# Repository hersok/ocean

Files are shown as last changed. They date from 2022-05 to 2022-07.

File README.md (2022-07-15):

# O.C.E.A.N. – Open-Hardware Concentration Estimation and Numeration

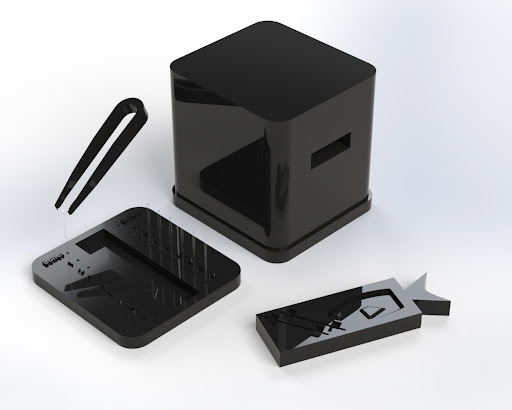
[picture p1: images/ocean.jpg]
Open-Hardware Concentration Estimation and Numeration
> 

### What is O.C.E.A.N.?

O.C.E.A.N. stands for Open-Hardware Concentration Estimation and Numeration.

O.C.E.A.N. is a low-cost, open-hardware device for measuring the concentration of liquid samples for cryogenic processing

### Why is concentration measurement important?

Concentration measurements ensure quality management at several crucial steps in the cryopreservation process.

### What is Open-Hardware?

Open-Hardware is an emerging movement in scientific research that aims to create freely available, iterative, and community-based designs for manufacturing labware, thereby lowering cost barriers to research.

### Why is the cryopreservation of fish and aquatic species' germplasm important?

1. Food security

2. Biomedical research

3. Genetic Biodiversity

### What is a short summary of this project?

Open-Hardware Concentration Estimation and Numeration, O.C.E.A.N., is an open-hardware device for measuring the cell concentration of fish germplasm samples to provide quality management in cryogenic research processes. The cryopreservation of fish and aquatic species’ germplasm is central to food security, biomedical research, and for maintaining genetic biodiversity. At present, the aquatic species cryopreservation process is impeded by the absence of low-cost, accessible devices for concentration measurement of low-volume samples. O.C.E.A.N. is an open-hardware device that seeks to address the current barriers to concentration measurement, as current methods may be expensive, time-intensive, and exclusive to select processing centers. Our device can be successfully used to generate a calibration curve for known concentrations. After generating this curve, the device makes it possible to measure the concentration of 5 µL fish sperm samples. The 3D Design files are openly available for download on GitHub, allowing for anyone with access to a 3D-printer, photocell, LED, and Arduino UNO board, to replicate and iterate on our results.

### Open-source License

This open hardware project is licensed by the Creative Commons `Attribution-NonCommercial-ShareAlike 4.0 International (CC BY-NC-SA 4.0)` License

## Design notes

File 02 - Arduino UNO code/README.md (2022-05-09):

# Arduino Code

## Background

For this project, our group used the following microcontrollers:

1. Arduino UNO

2. Arduino UNO WiFi Rev 2

---

## Uploading code files to Arduino Device

Please see the instructions below for how we uploaded `.ino` code files to the respective Arduino UNO boards:

### Connect the Arduino UNO device to your computer

1. Obtain a **USB-B to USB-A cable**

2. Connect one end to the Arduino UNO's USB-B port

3. Connect the other end to your computer's USB-port

### Uploading files to the Arduino UNO board

#### Arduino UNO

1. Download and install the Arduino IDE from https://www.arduino.cc/en/software

2. Open the Arduino IDE

3. Go to "File > Open" to open a particular file

4. Compile the code using the "Verify" checkmark button near the top of the IDE.

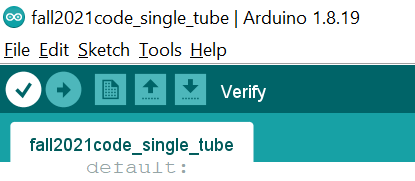
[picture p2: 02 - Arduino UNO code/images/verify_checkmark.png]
Compile the code using the Verify button
> 

5. Ensure that the Arduino UNO board is plugged into your computer via USB. Please see instructions [here](#Connect-the-Arduino-UNO-device-to-your-computer)

6. Ensure that the correct type of board is configured in the Arduino IDE

7. Go to "Tools > Board > Arduino AVR Boards > Arduino UNO "

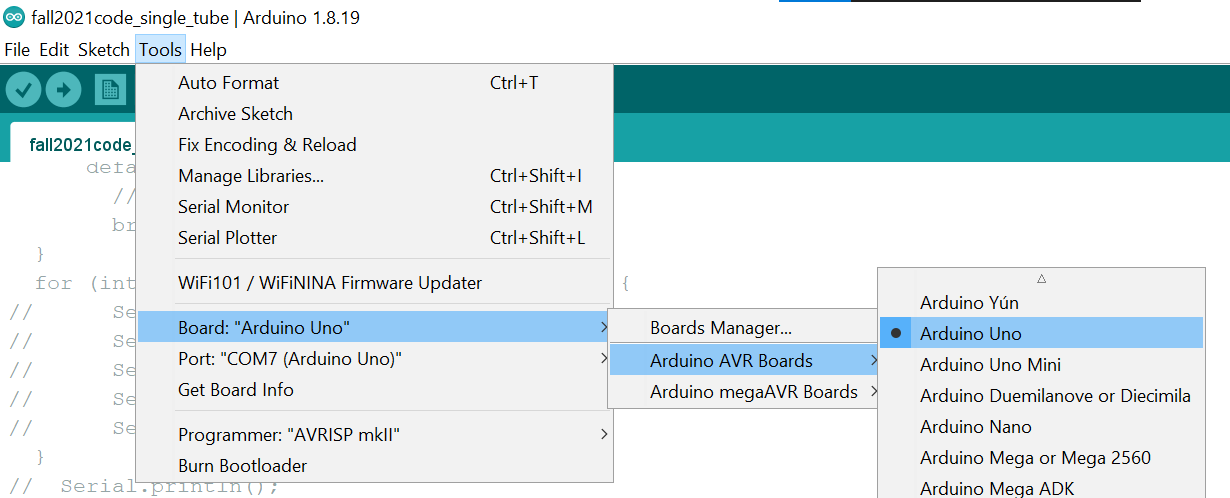
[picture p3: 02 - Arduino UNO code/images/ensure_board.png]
Select the appropriate board
> 

8. Ensure that the correct COM port is selected

9. Go to "Tools > Port" and select the Serial port alongside "Arduino UNO" in parentheses. For example, in the picture below, it is "COM7 (Arduino UNO)"

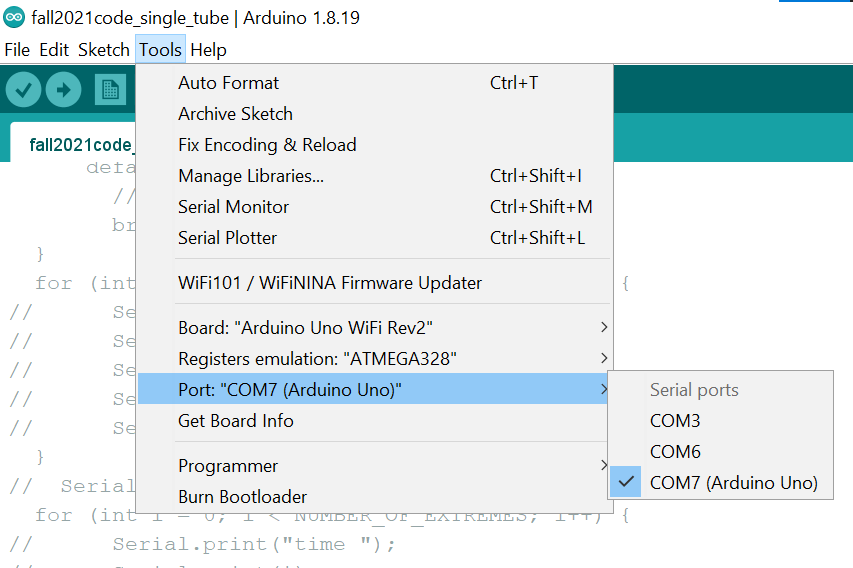
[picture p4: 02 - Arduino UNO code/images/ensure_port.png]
Select the appropriate port
> 

10. Upload the code to the Arduino UNO using the right-arrow upload button at the top of the page.

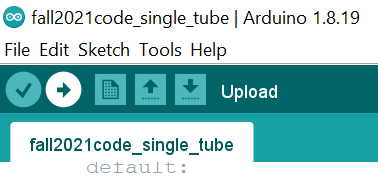
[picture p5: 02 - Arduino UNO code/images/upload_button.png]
> 

<!-- #### Arduino UNO WiFi -->

<!-- # Using KiTTY software to save Arduino Serial Monitor output -->

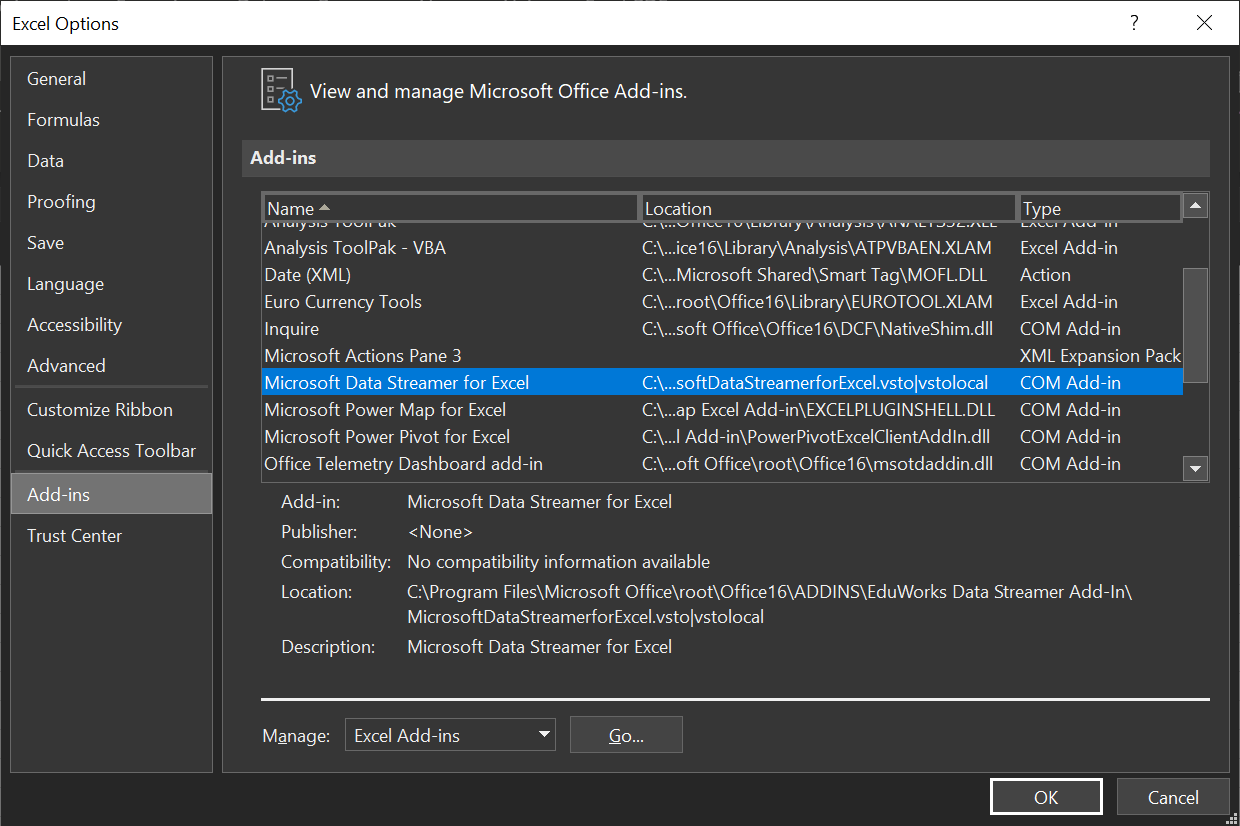
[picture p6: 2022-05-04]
02 - Arduino UNO code/images/excel data streamer option menu.png

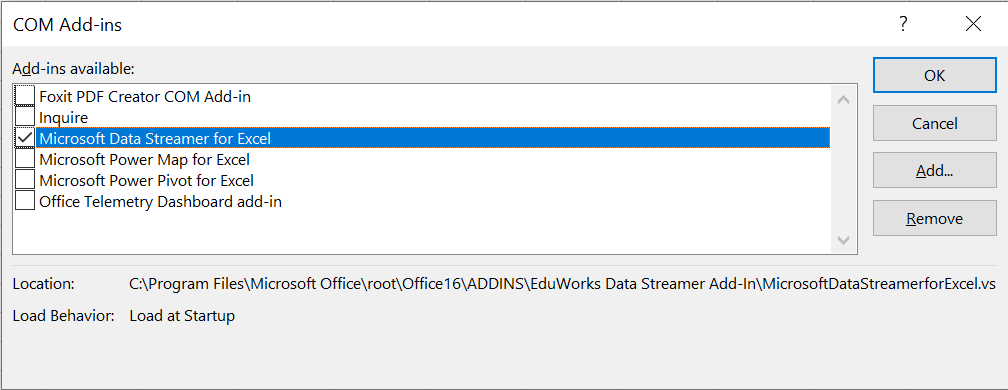
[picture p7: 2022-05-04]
02 - Arduino UNO code/images/dialog_box.png

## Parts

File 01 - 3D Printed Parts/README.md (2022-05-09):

# 3D Printed Parts

## Description

This folder contains all of the 3D-printed parts for O.C.E.A.N.

All parts were designed in SolidWorks

## Contents

This directory contains three folders, each with 13 parts:

1. `*.SLDPRT`

    * These are the original SolidWorks files. Please use these files if you would like to change an aspect of the design!

2. `*.STL`

    * The unit for these STL files is inches. Please use these files if you would like to print the device!

3. `*.3MF`

    * This is an alternative type of file for 3D printing that contains unit information.

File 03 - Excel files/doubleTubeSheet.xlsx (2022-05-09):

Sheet: userInterface
What are you measuring? |  | Do you already know the concentration? |  |  | What is your name?
Fish Sperm | solutions | Yes | is my answer |  | John Doe | is my name
What type of fish? |  | If yes, what's the type of concentration? |  |  | What is your affiliation?
Goldfish | is my fish type | Nominal | concentration |  | LSU AgCenter | is my lab's name
What is the purpose of your measurement? |  | What are the units of your concentration? |  |  | What is your Sample's ID number?
Calibration | is my intent | g/mL | are the units | C- | 100 | is the Sample ID
What is the volume of your sample? |  | What is your sample's concentration? |  |  | Data Streamer:
5 | uL | 0.2 | g/mL |  | Buffer: | 371
 |  |  |  |  | Sample: | 376

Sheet: calibrationData
Index | Date | Time | Buffer Peak | Sample Peak | Sample Type | Fish Type | Concentration Known | Concentration Type | Concentration | Units | Meas. Purpose | Sample Volume (uL) | User Name | Lab Name | Sample ID
1 | 2022-May-06 | 1899-12-30 | 371 | 376 | Fish Sperm | Goldfish | Yes | Nominal | 0.2 | g/mL | Calibration | 5 | John Doe | LSU AgCenter | C-100

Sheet: measurementData
Index | Date | Time | Buffer Peak | Sample Peak | Sample Type | Fish Type | Concentration Known | Concentration Type | Concentration | Units | Meas. Purpose | Sample Volume (uL) | User Name | Lab Name | Sample ID
1 | 2022-May-06 | 1899-12-30 | 371 | 376 | Fish Sperm | Goldfish | Yes | Nominal | 0.2 | g/mL | Measurement | 5 | John Doe | LSU AgCenter | M-100

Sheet: Data In
Data In (From Arduino Uno (COM7))
Data coming from the current data source will appear below as it is received.
Current Data
TIME | CH1 | CH2 | CH3 | CH4 | CH5 | CH6 | CH7 | CH8 | CH9 | CH10
44687.34931 | 371 | 376
Historical Data
TIME | CH1 | CH2 | CH3 | CH4 | CH5 | CH6 | CH7 | CH8 | CH9 | CH10
44687.34918 | 375 | 384
44687.34931 | 371 | 376

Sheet: Data Out
Data Out (To Device)
Data entered into the channels below will be sent to the currently connected device as a comma-delimited string.
CH1 | CH2 | CH3 | CH4 | CH5 | CH6 | CH7 | CH8 | CH9 | CH10

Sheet: Settings
Workbook Settings
Settings below will affect how data is read into the current workbook from data sources. Clear a field's contents to revert to its default setting.
Data interval (ms) | 150 | 150
Data rows | 15 | 15
Data channels | 10 | 10
Data orientation | Newest last | Newest last
WARNING: Changing settings may result in the loss of content and/or custom formatting in the Data In and Data Out worksheets. Always save before changing values.

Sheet: Manifest
Arduino Uno |  |  |  |  |  |  |  |  | {"Channels":[{"Description":null,"Id":null,"IsGhost":false,"Name":null,"Status":"Active","SubChannels":[{"Description":null,"Id":"CH1","IsGhost":false,"Name":"CH1","Status":"Active","SubChannels":[],"UnitOfMeasure":null},{"Description":null,"Id":"CH2","IsGhost":false,"Name":"CH2","Status":"Active","SubChannels":[],"UnitOfMeasure":null},{"Description":null,"Id":"CH3","IsGhost":false,"Name":"CH3","Status":"Active","SubChannels":[],"UnitOfMeasure":null},{"Description":null,"Id":"CH4","IsGhost":false,"Name":"CH4","Status":"Active","SubChannels":[],"UnitOfMeasure":null},{"Description":null,"Id":"CH5","IsGhost":false,"Name":"CH5","Status":"Active","SubChannels":[],"UnitOfMeasure":null},{"Description":null,"Id":"CH6","IsGhost":false,"Name":"CH6","Status":"Active","SubChannels":[],"UnitOfMeasure":null},{"Description":null,"Id":"CH7","IsGhost":false,"Name":"CH7","Status":"Active","SubChannels":[],"UnitOfMeasure":null},{"Description":null,"Id":"CH8","IsGhost":false,"Name":"CH8","Status":"Active","SubChannels":[],"UnitOfMeasure":null},{"Description":null,"Id":"CH9","IsGhost":false,"Name":"CH9","Status":"Active","SubChannels":[],"UnitOfMeasure":null},{"Description":null,"Id":"CH10","IsGhost":false,"Name":"CH10","Status":"Active","SubChannels":[],"UnitOfMeasure":null}],"UnitOfMeasure":null}],"Commands":[],"DataInterval":150,"Id":"3EB6B8E7-BFE3-4EF6-AA1D-74373D2929EC","IsGenerated":true,"Name":"Arduino Uno","Version":null,"BaudRate":115200}
This manifest was generated for the connected device. You can edit the device name and channel data here and the Data In worksheet will be updated.
 | Channels
 |  |  |  |  |  |  | Data Source Id
 |  | Id | Name | Description | Unit of Measure | Active | 3EB6B8E7-BFE3-4EF6-AA1D-74373D2929EC | 1
 |  | CH1 | CH1 |  |  | ü | Data Interval (ms)
 |  | CH2 | CH2 |  |  | ü | 150
 |  | CH3 | CH3 |  |  | ü | Baud Rate
 |  | CH4 | CH4 |  |  | ü | 115200
 |  | CH5 | CH5 |  |  | ü
 |  | CH6 | CH6 |  |  | ü
 |  | CH7 | CH7 |  |  | ü
 |  | CH8 | CH8 |  |  | ü
 |  | CH9 | CH9 |  |  | ü
 |  | CH10 | CH10 |  |  | ü

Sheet: menuOptions
Total Time Options | Sampling Options | Affliation Options | Measurement Type Options | Fish Options | Binary Options | Concentration Type Options | Concentration Units Options | Purpose Options | Volume Options | Concentration Options
1 | 1 | Louisiana State University | Powdered Milk | Zebrafish | Yes | Nominal | g/mL | Calibration | 1 | N/A
2 | 2 | LSU AgCenter | Fish Sperm | Catfish | No | Exact | cells/mL | Measurement | 2 | 3
5 | 5 |  |  | Salmon |  |  |  |  | 3 | 2
10 | 10 |  |  | Carp |  |  |  |  | 4 | 1
15 | 20 |  |  | N/A |  |  |  |  | 5 | 0.75
20 | 30 |  |  | Goldfish |  |  |  |  | 6 | 0.5
25 | 40 |  |  |  |  |  |  |  | 7 | 0.25
30 | 50 |  |  |  |  |  |  |  | 8 | 0.2
60 | 100 |  |  |  |  |  |  |  | 9 | 0.125
 |  |  |  |  |  |  |  |  | 10 | 0.1
 |  |  |  |  |  |  |  |  | 15 | 0.05
 |  |  |  |  |  |  |  |  | 20 | 0.025
 |  |  |  |  |  |  |  |  | 25 | 0.02
 |  |  |  |  |  |  |  |  | 30 | 0.01
 |  |  |  |  |  |  |  |  | 50

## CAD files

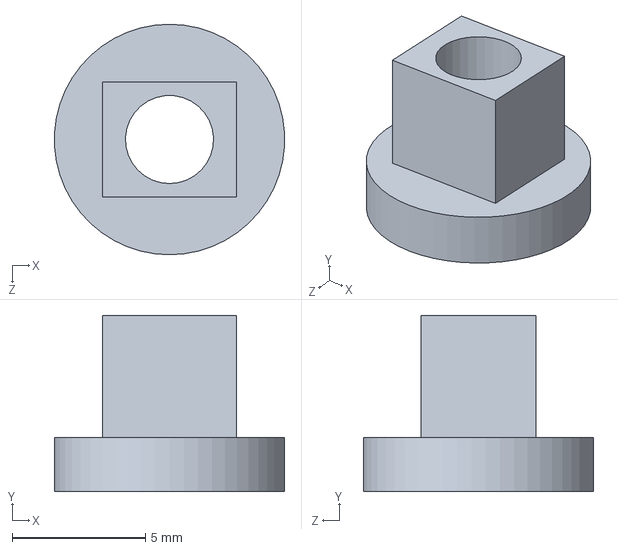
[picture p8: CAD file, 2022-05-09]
01 - 3D Printed Parts/SLDPRT/Sensor Cap.SLDPRT
8.62 x 6.60 x 8.64 mm

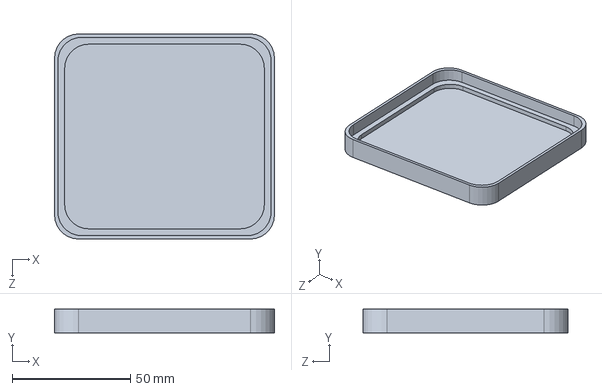
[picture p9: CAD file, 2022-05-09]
01 - 3D Printed Parts/SLDPRT/Base.SLDPRT
93.2 x 10.2 x 86.9 mm

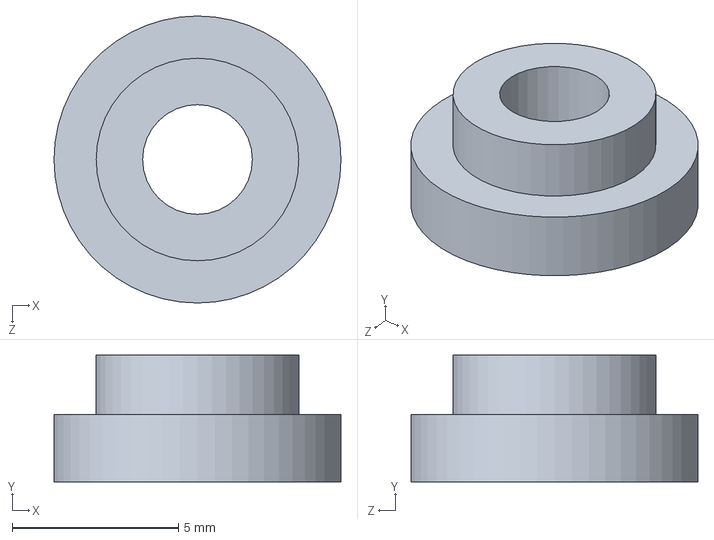
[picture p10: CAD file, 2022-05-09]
01 - 3D Printed Parts/SLDPRT/LED Cap.SLDPRT
8.64 x 3.81 x 8.64 mm

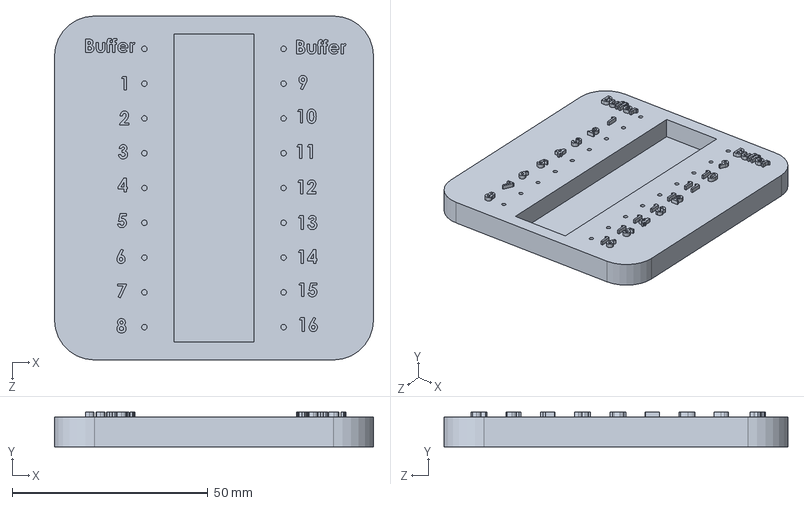
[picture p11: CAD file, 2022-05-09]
01 - 3D Printed Parts/SLDPRT/Tube Holding Tray.SLDPRT
81.5 x 8.89 x 87.9 mm

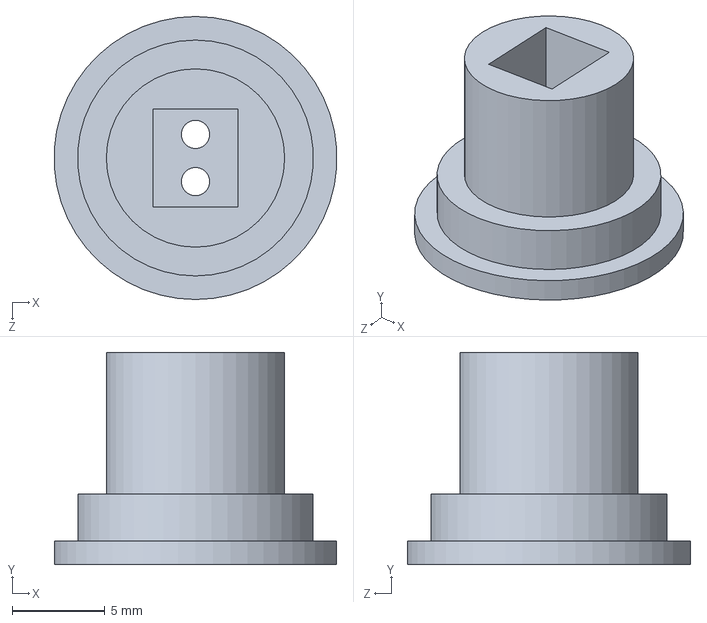
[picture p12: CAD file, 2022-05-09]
01 - 3D Printed Parts/SLDPRT/Sensor Holder.SLDPRT
15.2 x 11.4 x 15.2 mm

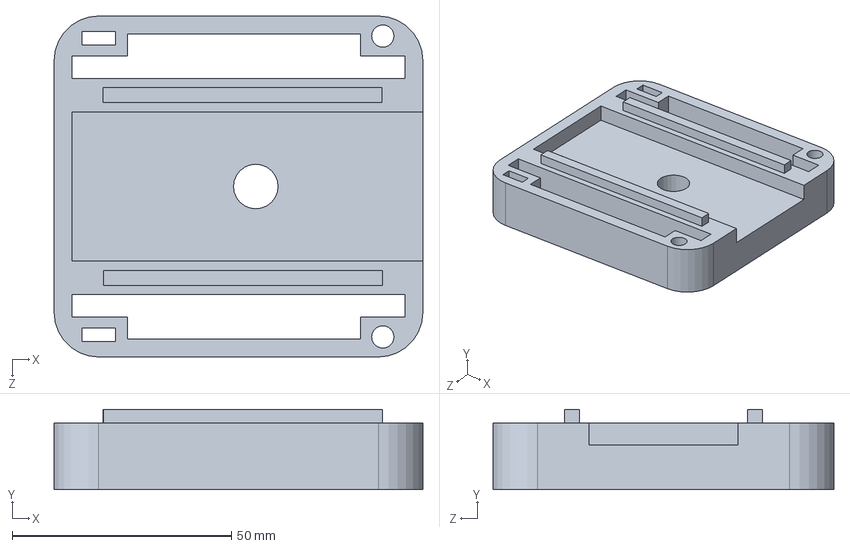
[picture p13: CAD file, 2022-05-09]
01 - 3D Printed Parts/SLDPRT/LED Shelf.SLDPRT
84.1 x 18.3 x 77.7 mm

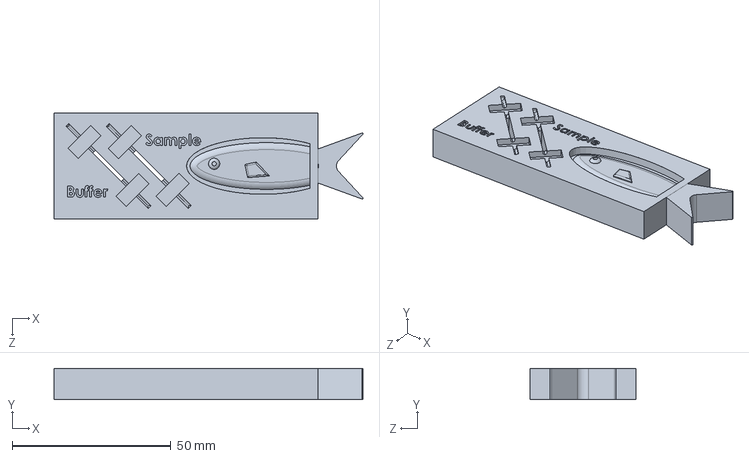
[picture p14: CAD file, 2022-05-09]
01 - 3D Printed Parts/SLDPRT/Tube Drawer.SLDPRT
97.3 x 9.91 x 33.4 mm

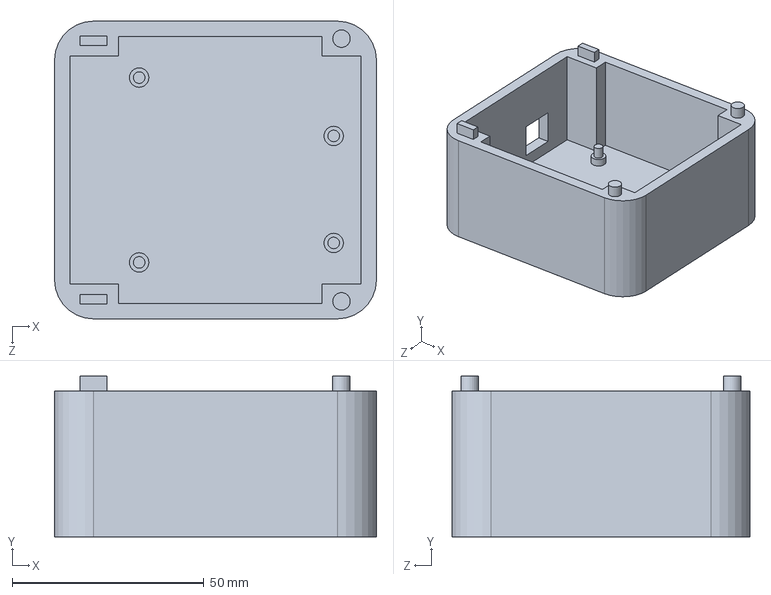
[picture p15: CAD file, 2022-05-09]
01 - 3D Printed Parts/SLDPRT/Arduino Shelf.SLDPRT
84.1 x 41.9 x 77.7 mm

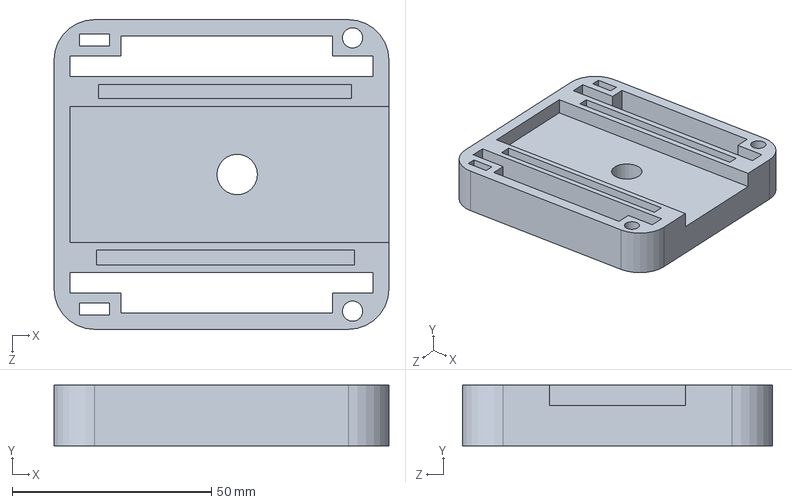
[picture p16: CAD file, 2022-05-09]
01 - 3D Printed Parts/SLDPRT/Sensor Shelf.SLDPRT
84.1 x 15.2 x 77.7 mm

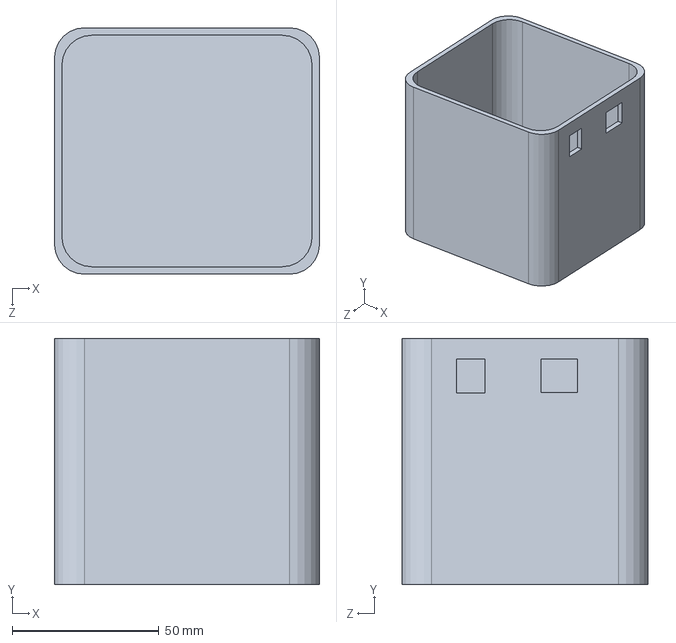
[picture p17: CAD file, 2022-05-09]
01 - 3D Printed Parts/SLDPRT/Cover.SLDPRT
90.4 x 84.1 x 84.1 mm

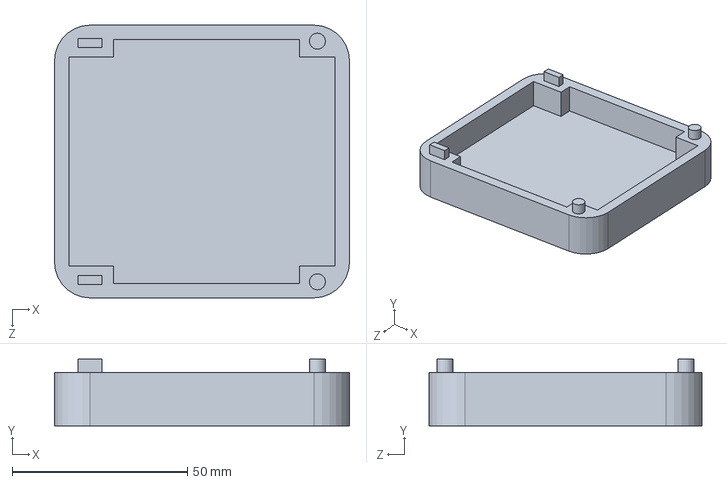
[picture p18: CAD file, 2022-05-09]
01 - 3D Printed Parts/SLDPRT/Top Shelf.SLDPRT
84.1 x 19.1 x 77.7 mm

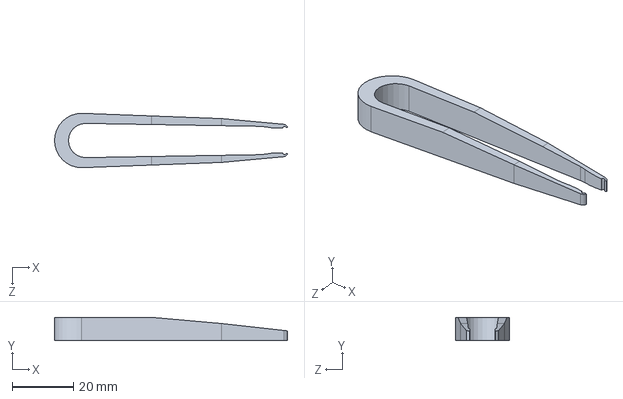
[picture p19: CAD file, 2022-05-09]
01 - 3D Printed Parts/SLDPRT/Tube Tweezer.SLDPRT
76.2 x 7.62 x 17.8 mm

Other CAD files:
01 - 3D Printed Parts/SLDPRT/LED Holder.SLDPRT
01 - 3D Printed Parts/3MF/Arduino Shelf.3MF
01 - 3D Printed Parts/3MF/Base.3MF
01 - 3D Printed Parts/3MF/Cover.3MF
01 - 3D Printed Parts/3MF/LED Cap.3MF
01 - 3D Printed Parts/3MF/LED Holder.3MF
01 - 3D Printed Parts/3MF/LED Shelf.3MF
01 - 3D Printed Parts/3MF/Sensor Cap.3MF
01 - 3D Printed Parts/3MF/Sensor Holder.3MF
01 - 3D Printed Parts/3MF/Sensor Shelf.3MF
01 - 3D Printed Parts/3MF/Top Shelf.3MF
01 - 3D Printed Parts/3MF/Tube Drawer.3MF
01 - 3D Printed Parts/3MF/Tube Holding Tray.3MF
01 - 3D Printed Parts/3MF/Tube Tweezer.3MF
01 - 3D Printed Parts/STL/Arduino Shelf.STL
01 - 3D Printed Parts/STL/Base.STL
01 - 3D Printed Parts/STL/Cover.STL
01 - 3D Printed Parts/STL/LED Cap.STL
01 - 3D Printed Parts/STL/LED Holder.STL
01 - 3D Printed Parts/STL/LED Shelf.STL
01 - 3D Printed Parts/STL/Sensor Cap.STL
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

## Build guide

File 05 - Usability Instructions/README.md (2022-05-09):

# Usability Instructions

## Preparing the device for measurements

1. Assemble the O.C.E.A.N. device as in the `04 - Assembly Instructions` folder.

2. Obtain glass microcapillary tubes to hold liquid samples. Our team used the following tubes:

    * Name: Drummond Scientific MicroCaps
    * Description: 100 Disposable 5μL micropipettes
    * CAT. No. 1-000-0050
    * Capacity: 5 μL
    * Length (mm): 32
    * Relative O.D.: 0.037 in
    * Relative I.D.: 0.0176 in
    * Manufacturer website: https://www.drummondsci.com/product/capillary-micropipettes/microcaps/

3. Upload the corresponding Arduino code file from the `02 - Arduino UNO code` folder. Instructions for how to upload are explained in the `README` file located in the same folder.

## Taking Measurements

1. Choose a method [here](#Saving-Results) for saving measurement results

2. Load a capillary tube containing your buffer solution into the designated slot on the testing drawer.

3. Load a capillary tube containing your sample into the designated slot.

4. Partially insert the testing drawer into the drawer slot until it does not fall out.

5. Open either the Arduino Serial Monitor or the provided MS Excel file

6. Ensure the Arduino UNO is plugged into the computer

7. Slowly insert the testing drawer into the device for a duration of 10 to 15 seconds. Slowly retract the testing drawer for a duration of 10 to 15 seconds.

8. Record the saved results, which should be in the output format of `Buffer Peak, Sample Peak`

## Saving Results

### MS Excel Data Streamer

1. Please follow the instructions linked below for how to "Enable the Data Streamer add-in" for MS Excel

> https://support.microsoft.com/en-us/office/enable-the-data-streamer-add-in-70052b28-3b00-41e7-8ab6-8a9f142dffeb

2. Download the `doubleTubeSheet.xlsx` file from the `03 - Excel files` folder

3. Open the `doubleTubeSheet.xlsx` file.

4. Navigate to the `Data Streamer` tab at the top of the Excel interface

5. Ensure the Arduino Uno is plugged into the computer

6. Select `Connect a Device` and click on the correct Arduino UNO device

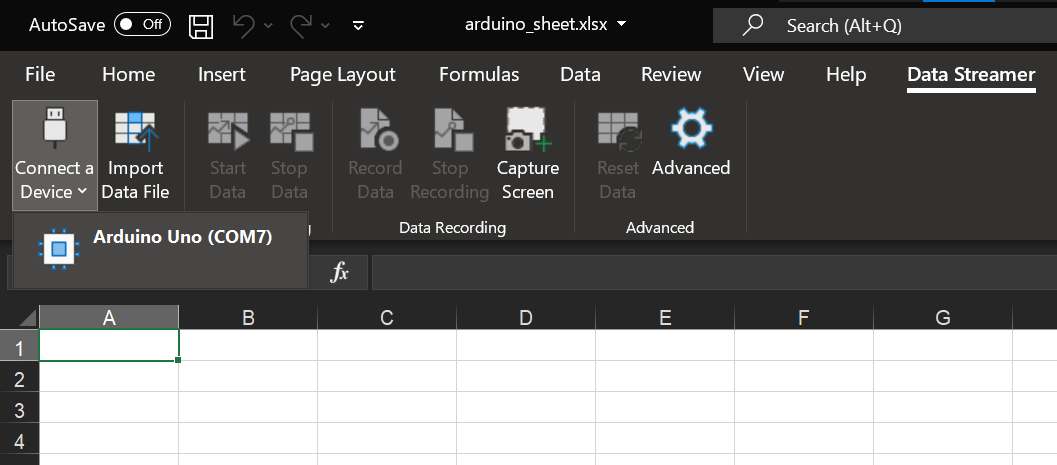
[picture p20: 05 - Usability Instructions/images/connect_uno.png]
Connect the Arduino UNO to MS Excel
> 

7. Press the `Advanced` settings cog > Navigate to `Settings tab` > Select the appropriate COM port > Change the Baud Rate to `115200`

8. Click on the `Start Data` button to begin collecting data

9. Navigate to the `userInterface` worksheet on Excel and change the values to your liking

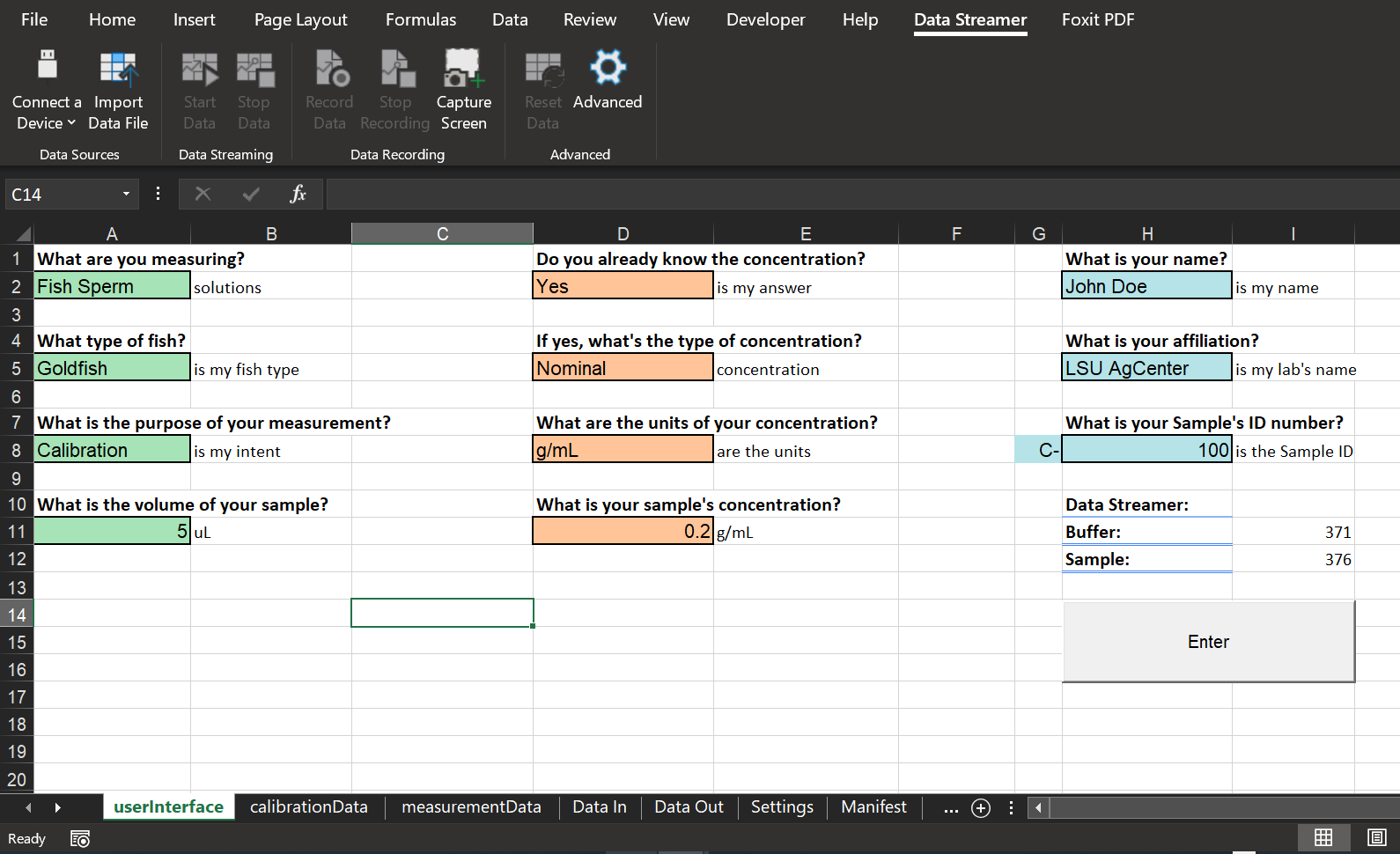
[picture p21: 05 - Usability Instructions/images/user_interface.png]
> 

10. Take a measurement per the instructions [here](#Taking-Measurements)

11. Press the Enter button

12. Navigate to either the `calibrationData` or `measurementData` worksheet to see your results

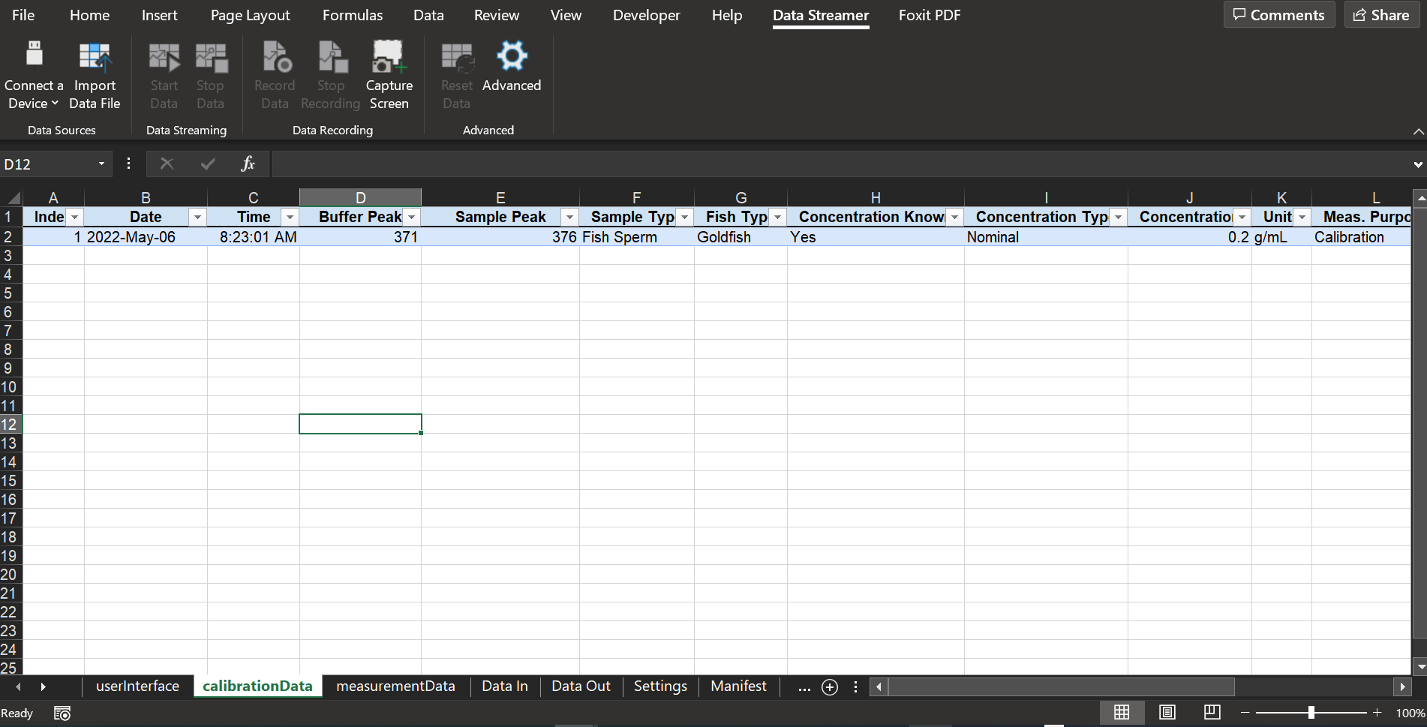
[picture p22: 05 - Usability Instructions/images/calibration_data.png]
> 

### Arduino IDE Serial Monitor

1. Open the Arduino IDE

2. Upload the corresponding Arduino code file from the `02 - Arduino UNO code` folder

3. Navigate to `Tools` > `Serial Monitor` to open the Serial Monitor

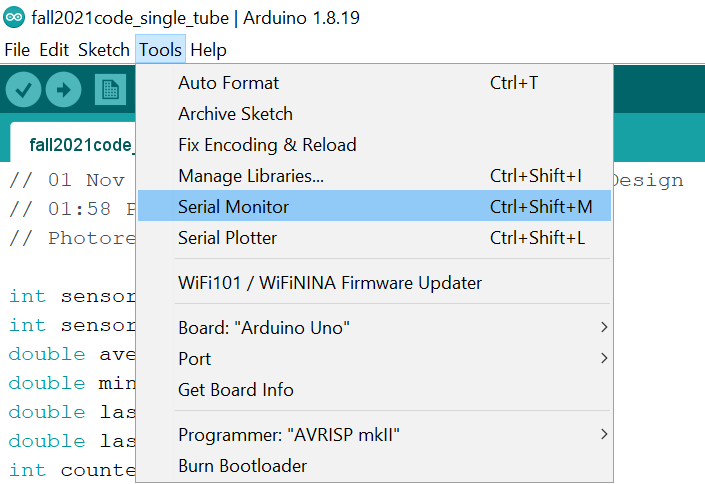
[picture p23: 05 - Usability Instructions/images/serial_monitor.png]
The Serial Monitor menu
> 

4. Ensure that the baud rates match by selecting the correct baud rate (115200 baud) from the dropdown menu in the lower right corner of the window.

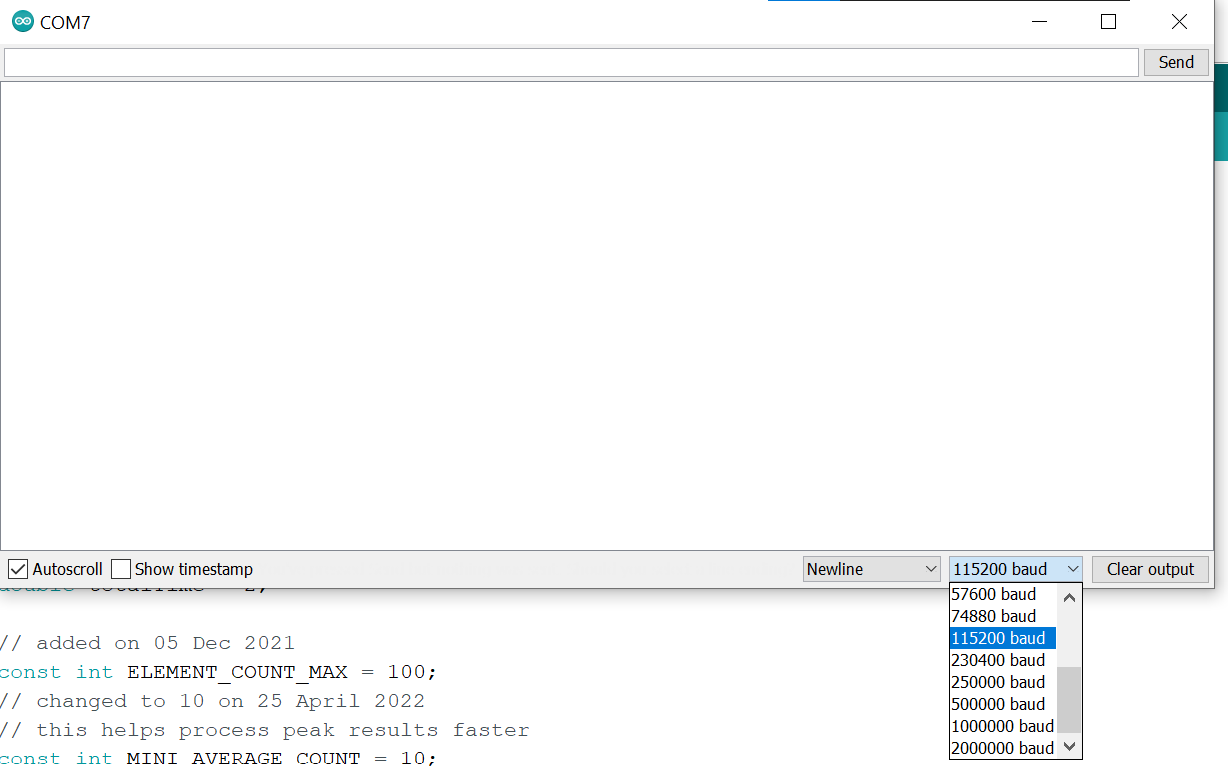
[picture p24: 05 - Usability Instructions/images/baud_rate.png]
Change the baud rate to 115200
> 

## 1. Creating a Calibration Curve

1. Follow the instructions in the [Taking Measurements](#Taking-Measurements) section to measure and record values for 10 to 16 different concentrations of the test sample.

2. Download and open the `calibrationDashboard` file from the `03 - Excel files` folder

3. Input the measured peak values for the buffer and sample solutions

4. Input the Offset and Sensitivity values from the best-fit curve into cells `J25` and `J28`

## 2. Measuring the Concentration of New Samples

1. With the `calibrationDashboard` file open in Excel, navigate to the `Detecting Concentrations for Solute #1`

2. Take a measurement (instructions [here](#Taking-Measurements)) of the solution you would like to know the concentration of

3. Input the measured `Max Buffer Peak` and `Max Sample Peak` into the corresponding cells on the spreadsheet to calculate the concentration

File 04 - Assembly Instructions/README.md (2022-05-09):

# Assembly Instructions

## Physical Device Assembly

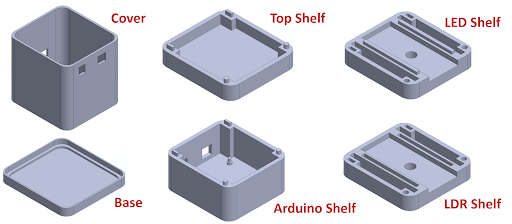
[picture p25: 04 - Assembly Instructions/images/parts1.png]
Parts Picture 1
> 

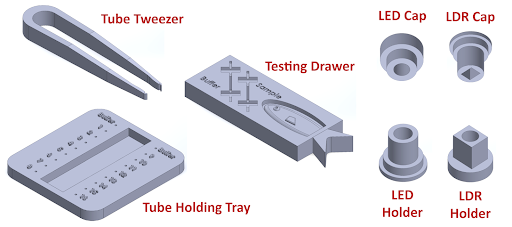
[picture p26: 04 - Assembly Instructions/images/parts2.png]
Parts Picture 2
> 

1. Install the Arduino UNO board onto the Arduino shelf, using the provided mounting features.

2. Assemble the breadboard circuit as shown. Our team used 20cm long female-to-male jumper wires in order to connect the LED and light-dependent resistor (LDR).

3. Install jumper wires leading from the breadboard to the Arduino UNO's `5V power`, `ground`, and `A0` ports.

4. First, install the LDR into the LDR Cap, then, assemble with the LDR Holder. Insert this subassembly into the LDR shelf.

5. Assemble the LDR shelf to the top of the Arduino shelf. These parts have asymmetrical mating features so that the parts can only be assembled one way...the right way!

6. First, install the LED into the LED Cap, then, assemble with the LED Holder. Insert this subassembly into the LED shelf.

7. Assemble the LED shelf to the top of the LDR shelf.

8. Assemble the top shelf to the existing assembly.

9. Move the existing assembly to rest on the base piece.

10. Assemble the cover so that it covers the existing assembly and snaps into the base.

11. Get ready to measure concentrations!

## Circuit Assembly

### Circuit Diagram

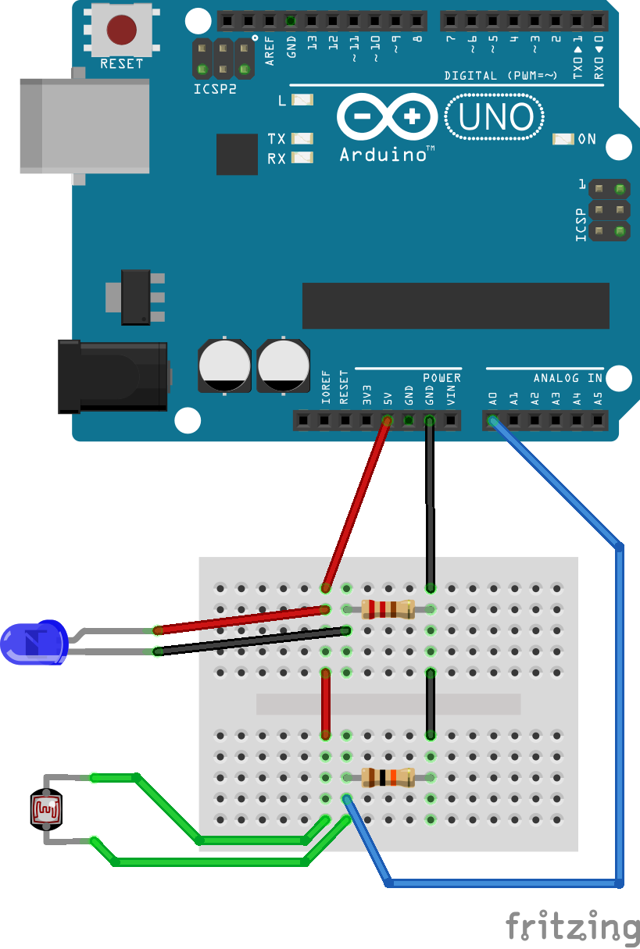
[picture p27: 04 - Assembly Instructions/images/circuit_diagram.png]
Arduino Circuit assembly
> 

### Circuit Schematic

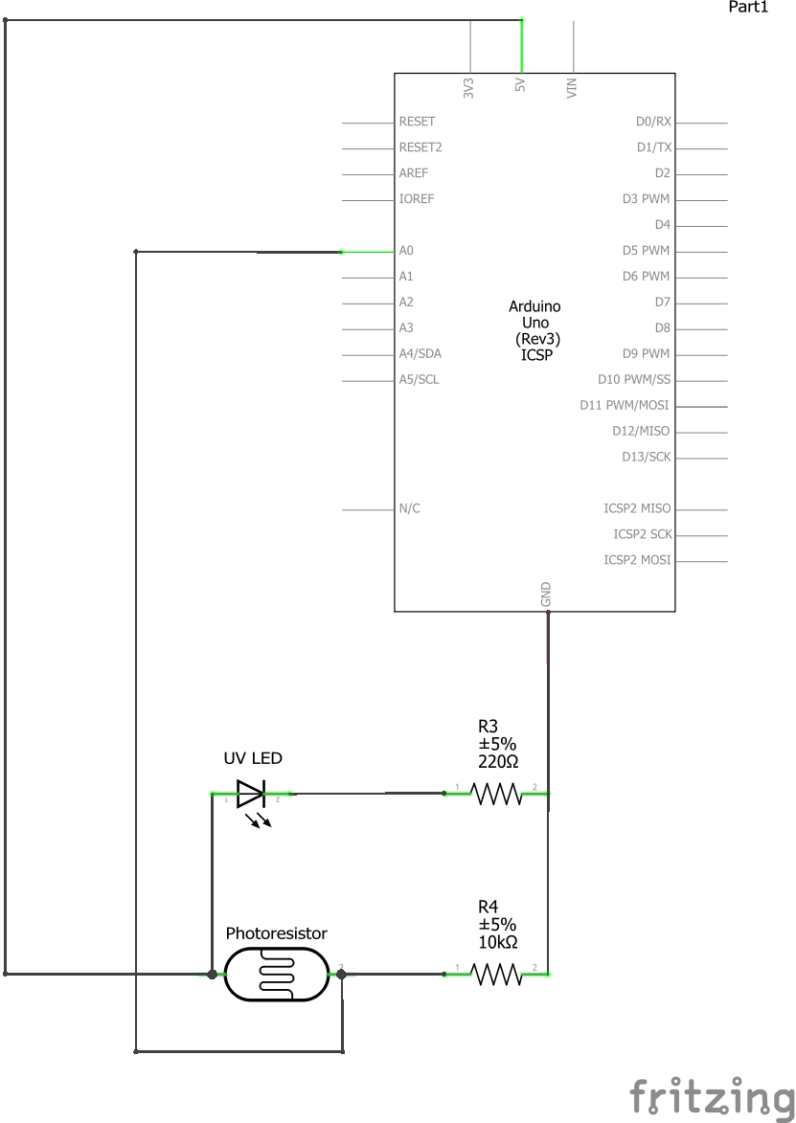
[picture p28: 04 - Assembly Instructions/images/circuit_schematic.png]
Arduino Circuit schematic
> 

### Parts required

1. UV LED (watch out for the direction of the positive lead!)

2. Light-dependent resistor

3. 100-300 Ohm resistor (220 Ohm in our case)

4. 5000-10000 Ohm resistor (10k Ohm in our case)

5. Wires (we used a combination of male-to-male and female-to-male 20cm long jumper wires)

6. Arduino UNO board

7. USB-B to USB-A cable

8. Breadboard (the above diagram is for a mini breadboard, which fits inside the device. However, the circuit may be assembled without the help of a breadboard, so long that the photocell and LED are connected in parallel, as shown in the schematic above.)

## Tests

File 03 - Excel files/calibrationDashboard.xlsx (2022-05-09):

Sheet: Calibration for Solute #1
 | Table 1 | Sperm Cells / mL
Step 1: Calibrate Device for Solute | Concentration # | Known Concentration | Max Buffer Peak | Max Sample Peak | Date | Time
Use solute that you seek to determine concentration of in future use of device (ex. powdered milk, specific species) | 1 | 4800000000 | 393 | 105 | 2022-05-04 | 13:03:01
 | 2 | 2400000000 | 375 | 135 | 2022-05-04 | 13:28:43
1. Use up to 16 known sample concentrations to calibrate device. More known concentrations = better calibration | 3 | 1200000000 | 395 | 204 | 2022-05-04 | 13:30:10
 | 4 | 600000000 | 389 | 278 | 2022-05-04 | 13:32:17
2. Collect each sample concentration with seperate capillary tubes and put in numbered slots on holding tray | 5 | 300000000 | 388 | 329 | 2022-05-04 | 13:34:39
 | 6 | 150000000 | 397 | 350 | 2022-05-04 | 13:35:14 | All 14
3. Collect buffer or solvent in a capillary tube and put in "buffer" slot on test drawer | 7 | 75000000 | 390 | 370 | 2022-05-04 | 13:42:05
 | 8 | 37500000 | 393 | 368 | 2022-05-04 | 13:44:49
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

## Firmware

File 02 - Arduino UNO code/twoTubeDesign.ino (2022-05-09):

//
// Copyright 2022
//
// publish date: 03 May 2022, Tuesday, at 11:41 AM
// version 1 of code
// to do: add timestamp to output
//
// this code:
// outputs peak values for the two-tube design
//

int sensorPin = A0;
int sensorValue = 0;
double valuesAverage = 0;
int counter = 0;
double delayVal = 1000;
// total time for testing (in seconds)
double totalTime = 0.1;

const int ELEMENT_COUNT_MAX = 100;
// the sampling time is totalTime / ELEMENT_COUNT_MAX
// for example, this code takes measurements every 0.1/100 = 0.001 seconds
double values[ELEMENT_COUNT_MAX];

const int NUMBER_OF_EXTREMES = 4;
double extremes[NUMBER_OF_EXTREMES];
double times[NUMBER_OF_EXTREMES];

// when the sensorValue crosses the monitoringThreshold,
// the code starts to look for peak values to record
const double monitoringThreshold = 0.03;
double thresholdValue = 0;
int maxValue = 0;
int numberOfPeak = 0;
double lastAverage = 0;
bool resetTracker = true;
int currentIndex = 0;

void setup() {
  Serial.begin(115200);
  for (int i = 0; i < ELEMENT_COUNT_MAX; i++) {
   values[i] = 0;
  }
  delayVal = delayVal / (ELEMENT_COUNT_MAX/totalTime);
}

void loop() {
  sensorValue = analogRead(sensorPin);
  delay(delayVal);
  counter = counter + 1;
  // debugging purposes: prints out the sensor value
  // Serial.println(sensorValue);

  valuesAverage = valuesAverage + sensorValue;
  values[counter - 1] = sensorValue;

  // once the values array is full,
  // this calculates the average of its values
  if (counter == ELEMENT_COUNT_MAX) {
    valuesAverage = valuesAverage / counter;
    lastAverage = valuesAverage;
    valuesAverage = 0;
    counter = 0;
  }

// switch statement that coordinates the logic for saving peak values
  switch (numberOfPeak) {
      case 0:
          if (sensorValue > maxValue) {
              maxValue = sensorValue;
          }
          thresholdValue = (maxValue - 0) * monitoringThreshold;
          if (sensorValue < thresholdValue) {
              if ((lastAverage - sensorValue) > 0) {
                  numberOfPeak = 1;
              }
          }
          break;
      case 1:
          // Serial.println("You crossed the threshold, going from high to low");
          if (resetTracker) {
              maxValue = 0;
              resetTracker = false;
          }
          if (sensorValue > thresholdValue) {
              if ((lastAverage - sensorValue) < 0) {
                  numberOfPeak = 2;
              }
          }
          break;
      case 2:
          // Serial.println("You crossed the threshold, going from low to high");
          if (sensorValue > maxValue) {
              maxValue = sensorValue;
          }
          if (sensorValue < thresholdValue) {
              if ((lastAverage - sensorValue) > 0) {
                  if (currentIndex == 4) {
                      currentIndex = 0;
                      resetTracker = true;
                      numberOfPeak = 0;
                  } else {
                      extremes[currentIndex] = maxValue;
                      currentIndex++;
                      maxValue = 0;
                  }
                  numberOfPeak = 1;
              }
          }
          break;
      default:
        // do nothing
        break;
  }
  // if the peaks array is full,
  // then print the output and reset the array
  if (extremes[3] != 0) {
    printToSerial();
    for (int i = 0; i < NUMBER_OF_EXTREMES; i++) {
      extremes[i] = 0;
    }
  }
}

void printToSerial() {
// debugging code: prints all four peaks
 /*
  for (int i = 0; i < NUMBER_OF_EXTREMES; i++) {
      Serial.print(extremes[i]);
      if (i != 3) {
        Serial.print(",");
      }
    }
 */
  // Serial.println();
  // output has format: (1) buffer max (2) sample max
  Serial.print(max(extremes[0],extremes[3]));
  Serial.print(",");
  Serial.print(max(extremes[1],extremes[2]));
  Serial.println();
}

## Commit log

2022-05-04 Arduino instructions
2022-05-04 Arduino Uno code files
2022-05-09 3D printing file upload: STL, SLDPRT, 3MF
    [Arduino Shelf.3MF, Arduino Shelf.SLDPRT, Arduino Shelf.STL, Base.3MF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]
2022-05-09 Assembly instructions
2022-05-09 Microsoft Excel files
    To access and save DataStreamer results from MS Excel
    [doubleTubeSheet.xlsx]
2022-05-09 Modify file structure
    [doubleTubeSheet.xlsx]
2022-05-09 Updated files
    [calibrationDashboard.xlsx]
